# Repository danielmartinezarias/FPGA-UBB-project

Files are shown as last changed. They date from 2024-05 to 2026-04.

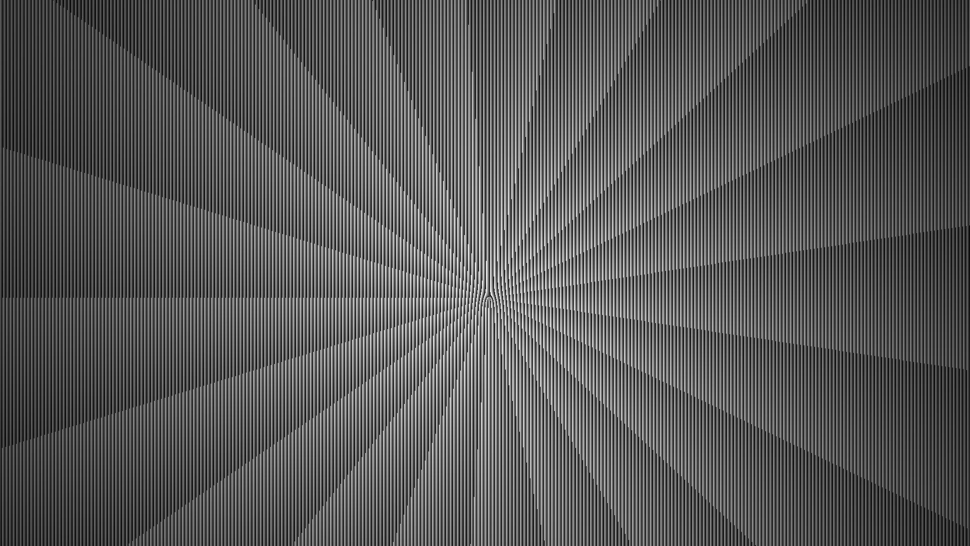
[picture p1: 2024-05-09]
Figuras_Hologramas_OAM/LG_3.jpeg

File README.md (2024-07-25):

# FPGA UBB Quantum Optics Lab
FPGA project for the control system of the OAM experiment. FPGA stores a set of images in a DDR memory, displays such images via HDMI port, prepares a train of short pulses to drive an EOM Intensity modulator, and aquires counts from 2 detectors. This project is meant to work along a GUI written in C#.

1. **electronics** contains the source files for the FMC PCB and the LM7171 AMP PCB. These includes manufacturing files, schematics and PCB outlines
2. **caja** contains a blender file with the mechanical drawings of the plastic box for the project
3. **Figuras_Hologramas_OAM** contains a set of holograms to display, and some images with numbers for calibration
4. **FPGA-Vivado-Project** contains the main Vivado project in `Genesys2_VideoDemoR1` and its sources in `srcs`. You can use the project as it is ot build the project by your own running the *srcs/Genesys2_VideoDemoR1.tcl* file with their respective dependencies and then build your own project. Synthesis, implementation and bitstream generation
5. **GUI** includes the main Graphical User Interface (GUI) to run the program along with the FPGA project. C# project in `SOFTWARE BASE-UART` and final GUI in `FINAL`. Notice that a USB UART connection is required to transmit information from the FPGA to PC 115200 buad rate.

## GUI
C# project in `GUI\SOFTWARE BASE-UART\` and FINAL Graphical User  Interface (GUI), located in `GUI\SOFTWARE BASE-UART\driver_PM_software\bin\Debug\driver_PM_software.exe`
**GUI controls**
- SOON TO BE UPDATED

## FPGA
- Main Vivado project in `FPGA-Vivado-Project\Genesys2_VideoDemoR1`, 
    - Final bitstream is located in `FPGA-Vivado-Project\Genesys2_VideoDemoR1\Genesys2_VideoDemoR1.runs\impl_1\*.bit`. 
    - You can upload this file into the FPGA using Vivado. Left bottom menu, PROGRAM AND DEBUG, Open Hardware, Auto connect, Program FPGA (with the .bit file)
- `srcs` contains all verilog files, please keep this updated

### How to use this repo?
- Create a GitHub account
- Download Github desktop
- CLONE the repository (ask me for access since it is a private repo)
    - If you want to use this files and not modify them CLONE this repository in the MAIN branch. 
    - If you want to modify it create a new branch and have fun
- Now all the files are in the folder where you cloned the repo.
- If you want to make permanet changes to the MAIN branch, make a commit, but ask me first
- GitHub is not meant to store experiment data, but code, keep this repo as clean as possible.

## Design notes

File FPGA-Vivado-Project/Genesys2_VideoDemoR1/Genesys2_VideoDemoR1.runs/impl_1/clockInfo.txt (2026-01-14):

-------------------------------------
| Tool Version : Vivado v.2023.2
| Date         : Wed Jan 14 18:05:04 2026
| Host         : LAPTOP-RR96MLV1
| Design       : design_1
| Device       : xc7k325t-ffg900-2--
-------------------------------------

For more information on clockInfo.txt clock routing debug file see https://support.xilinx.com/s/article/000035660?language=en_US

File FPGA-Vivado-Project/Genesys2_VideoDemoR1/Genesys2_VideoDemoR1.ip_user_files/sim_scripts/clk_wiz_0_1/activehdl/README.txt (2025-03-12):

################################################################################
# Vivado (TM) v2023.2 (64-bit)
#
# README.txt: Please read the sections below to understand the steps required to
#             run the exported script and how to fetch design source file details
#             from the file_info.txt file.
#
# Generated by export_simulation on Wed Mar 12 15:34:58 +0100 2025
#
################################################################################

1. Steps to run the generated simulation script

From the shell prompt in the current directory, issue the following command:-

./clk_wiz_0.sh

This command will launch the 'compile', 'elaborate' and 'simulate' functions
implemented in the script file for the 3-step flow. These functions are called
from the main 'run' function in the script file.

The 'run' function first calls the 'check_args' function, the purpose of which
is to verify the generated script arguments and print error if incorrect switch
is specified. The 'run' function then calls the 'setup' function, the purpose of
which is to specify custom or initialization commands. The function also executes
following sub-functions:-
'reset_run' if -reset_run switch is specified.
'reset_log' if -reset_log switch is specified.

The purpose of 'reset_run' function' is to delete the simulator generated design
data from the previous run and the purpose of 'reset_log' function' is to delete
the simulator generated log files.

The 'run' function then calls the 'init_lib' function, the purpose of which is to
create design library mappings and directories. This function is called before the
'compile' step. By default, if '-step' switch is specified with the script then the
script will execute that specfic step, else it will execute all steps applicable
for the target simulator.

For more information on the script, please type './clk_wiz_0.sh -help'

2. Design source file information

export_simulation generates a 'file_info.txt' file that contains design file information
based on the compile order when export_simulation was executed from Vivado. The file
contains information about the file name, type, library it is compiled into, whether
it is part of the IP, associated library, file path information in a comma separated
format. This file can be parsed to extract the required information for generating a
custom script or can be read from verification test infra.

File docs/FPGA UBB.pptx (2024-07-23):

## FPGA UBB

11-03-2024

## Genesys2_VideoDemoR1

- Display_clocks
  - Senales de reloj para video
- Dpti_ctrl
  - Interfaz entre USB-JTAG y memoria DDR para imagenes
- DDR
  - Memoria para guardar 112 imagenes 1920x1080p
- DVID
  - Video interface (HDMI)
- VideoLineBuffer
  - Video buffer
- Video_sync_gen
  - Video signals

## Genesys2_VideoDemoR1

- Sync_pulse_det
  - Genera el sync general, el pulso para el intensity mod (y el trigger para det pero esta obsoleto)
- PmodDA2
  - Controla el bias para el intensity modulator
- Tick_gen
  - Controla el reloj para la comunicacion serial
- UART_RX
  - Recibe parametros del computador via el USB-UART
- UART_Tx
  - Envia datos desde la FPGA hasta el PC
- Control_Parametros
  - Actualiza los parametros dentro de la FPGA
- AccCuentas
  - Adquiere la data de los detectors y suma un cierto numero de eventos en un registro
- Control_DM
  - Controla la secuencia del experimento

## Control_DM

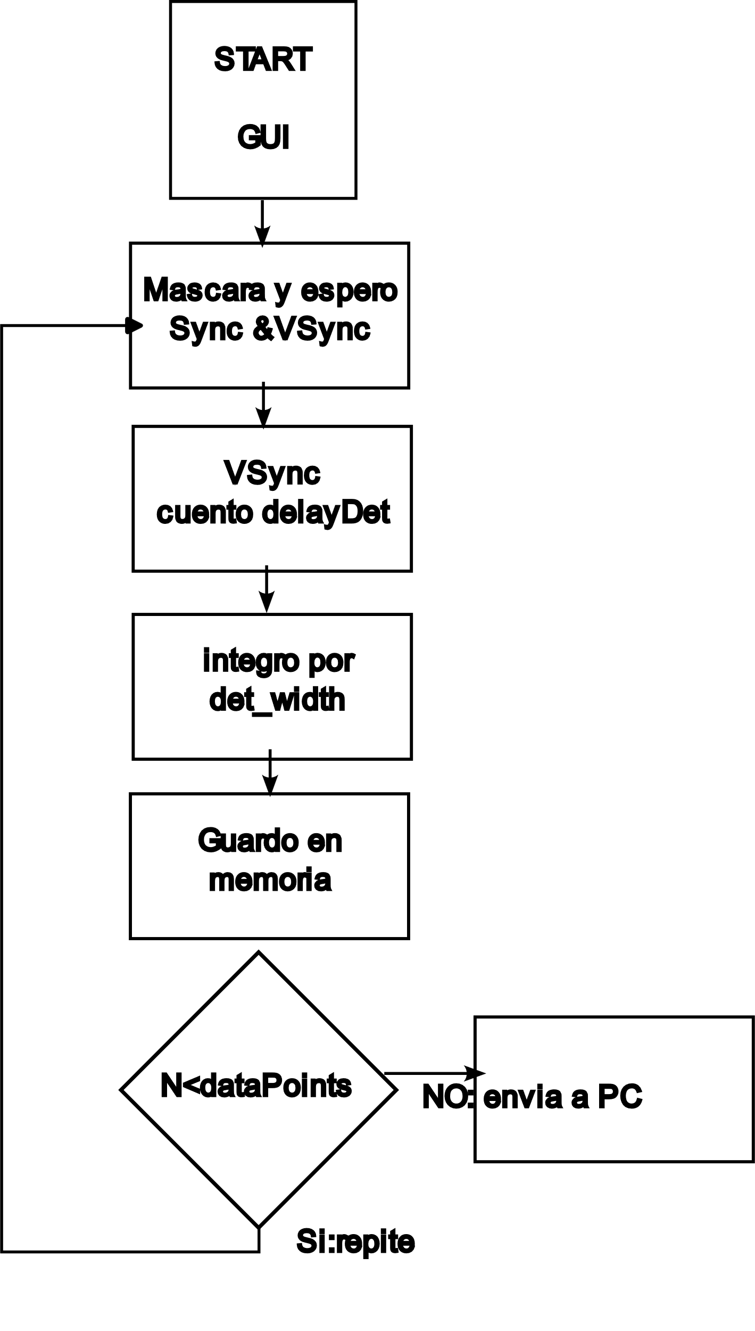
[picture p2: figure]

Falta la generacion del pulso …

## TO DO

- Definir cuantos pulsos por frame/ 1 pulso por frame pero dejar listo para hacer N pulsos por frame
- Necesitamos info pulso a pulso? Si
- Como muestro la data en programa? Se queda en standby
- Pendiente Cargar secuencia aleatoria de sequre

## Daniel

- PCB FMC mezzanine para mejorar data
- Hacer en eurocircuits y comparer project con Gustavo
- Sincronizar las FPGA
- Crear Proyecto en github

## Cristobal

- Cargar el bitstream FPGA_UBB\Final_FPGA_UBB\Genesys2_VideoDemoR1\Genesys2_VideoDemoR1.runs\impl_1\Genesys2_VideoDemoR1.bit en la FPGA
- Correr el GUI que esta en \FPGA_UBB\Final_FPGA_UBB\SOFTWARE BASE-UART\driver_PM_software\bin\Debug\ driver_PM_software.exe

## Cristobal (Para pulso optico)

- Colocar SW(0) = 1
- En GUI Start, luego Monitorear el Puerto LA18_P_CC en osciloscopio. Debe ser pulso cuadrado aprox 1.8V, frecuencia dada por el parametro en GUI. Luego pasar el pulso por el AMP y ajustar para IM.
- Pulsar el IM, evaluar la maxima velocidad, detectando con un fotodiodo y visualizando con osciloscopio

## Cristobal (detector)

- Usar un generador de funciones, preparar un pulso 0-1.8V corto, parecido al pulso que genera el IDQCube, f = 1MHz, output pulse width = 10 ns. Conectar a LA01_PCC (det0) y en el GUI click en START. Width_det = 10000 (10us). Deberias ver 10 cuentas en el GUI
- Repetir conectando en el siguiente Puerto de entrada LA01_P_CC (en realidad es LA17)(det1)

## 27.06.23

- Cristobal probo y valido las detecciones.
- Habia un bug relacionado al reloj pero ya se arreglo

## 28.06.24

- Alice con SW0 = 1, BOB SW0 = 0
- Conectar sync(fmc_la_p_00) de ALICE a sync_ext(fmc_la_p_32) de BOB para que la senal sync de Alice vaya a Bob
- En Alice monitorear el sync(fmc_la_p_04) y MZI(fmc_la_p_18) en osciloscopio. Usar sync como trigger
- En Bob monitorear el det (fmc_la_p_24) que corresponde al tiempo de medicion.
- Ajustar el delay_pulse hasta que alcance a det

## 28.06.24

- Conectar el laser, modulador de intensidad, senal MZI y BIAS
- Conectar detector, y usar en modo trigger
- Mover el delay_det hasta que se maximizen las cuentas

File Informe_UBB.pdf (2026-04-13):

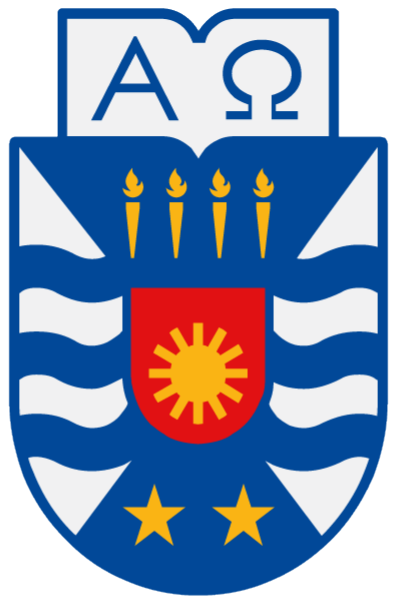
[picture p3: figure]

# Uso del Software de Control

Cristóbal Melo Dospital y Daniel Martinez

1 de abril de 2025

Universidad del Bío-Bío

### Índice

1. Introducción | 2
2. Uso de GitHub Desktop para clonar y mantener actualizado el proyecto | 2
2.1. Clonar el repositorio | | 2
2.2. Sincronizar el repositorio | | 3
2.3. Subir cambios al repositorio | | 4
3. Funcionamiento del Programa | 4
4. Carga del Bitstream a la FPGA | 5
5. Pinout de la Tarjeta FMC | 7
5.1. Salidas desde Alice | | 7
5.2. Entradas hacia Bob | | 7
6. Uso del Software de Control | 8
6.1. Conexión al puerto COM | | 8

### 1. Introducción

Este informe tiene como objetivo documentar el funcionamiento general del programa desarrollado para el control de señales en una FPGA, incluyendo el proceso de carga del bitstream y el uso de la interfaz de software.

### 2. Uso de GitHub Desktop para clonar y mantener actualizado el proyecto

A continuación se detallan los pasos para clonar un repositorio, sincronizar cambios y mantener actualizado el proyecto:

### 2.1. Clonar el repositorio

Opción A: Clonar usando GitHub Desktop vía URL

1. Abre GitHub Desktop.
2. En la barra superior, haz clic en File >Clone repository.

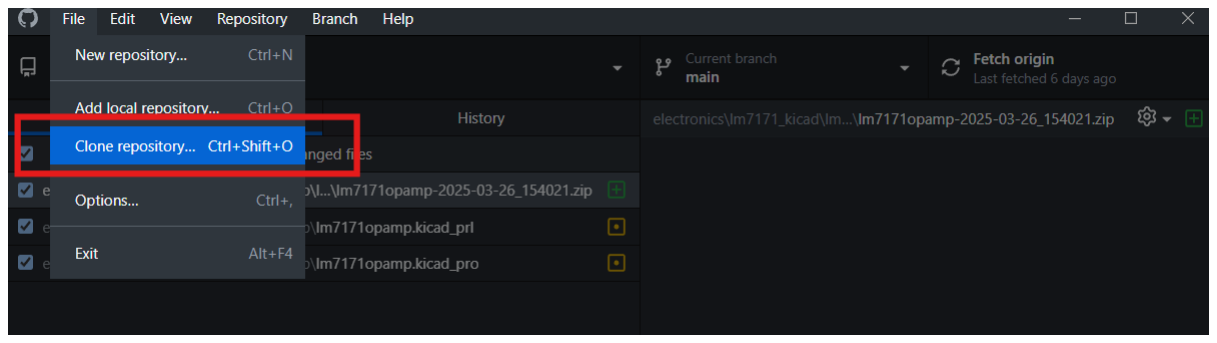
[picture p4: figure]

Figura 1: Clone repository usando Github Desktop

3. En la pestaña URL, pega la dirección del repositorio que deseas clonar (por ejemplo:

https://github.com/usuario/proyecto.git

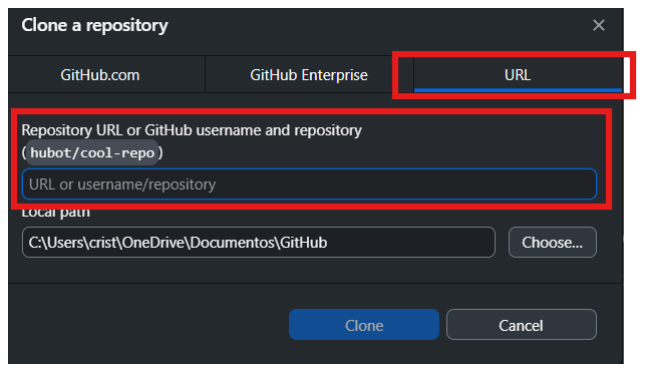
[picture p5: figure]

Figura 2: Ejemplo de clonar repositorio utilizando URL

4. Selecciona la ubicación en tu computador donde se guardará el repositorio localmente.
5. Haz clic en Clone.

Opción B: Clonar directamente desde GitHub.com (usando cuenta vinculada)

1. Abre GitHub Desktop e inicia sesión con tu cuenta de GitHub.
2. Haz clic en File >Clone repository.
3. En la pestaña GitHub.com, aparecerá automáticamente la lista de proyectos disponibles para clonar desde tu cuenta.

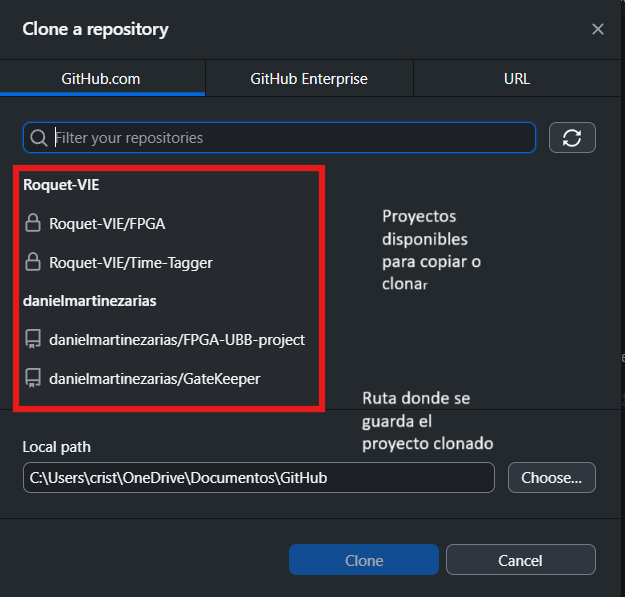
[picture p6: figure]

Figura 3: Ejemplo de clonar repositorio utilizando proyectos de Github.com

4. Selecciona el repositorio que desees clonar de la lista.
5. Elige la carpeta local donde se almacenará el proyecto.
6. Haz clic en Clone.

### 2.2. Sincronizar el repositorio

Una vez clonado, puedes sincronizar tu repositorio local con la versión para ver si hay cambios nuevos (pull) o si puedes subir tus cambios (push).

Presiona el botón Fetch origin en la parte superior. Esto verifica si hay cambios en el repositorio remoto.

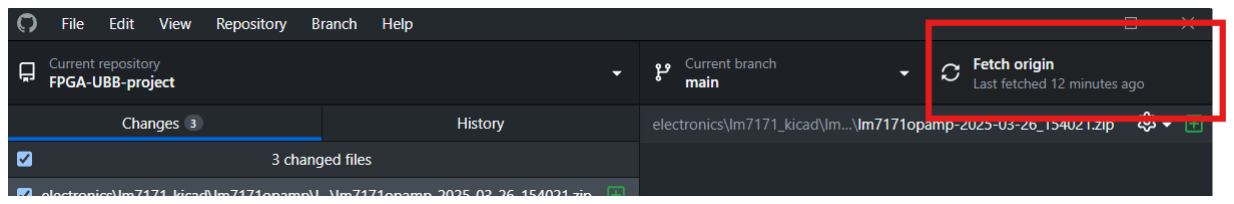
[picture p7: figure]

Figura 4: Sincronizar el repositorio.

Si existen nuevos archivos o modificaciones, el botón cambiará a Pull origin. Haz clic en él para traer los cambios a tu computador.

Si se realizo cambios en tu computador (por ejemplo, editaste archivos del proyecto de Vivado), verás la opción de Commit to main y luego Push origin para subirlos a GitHub (ver Fig. 5).

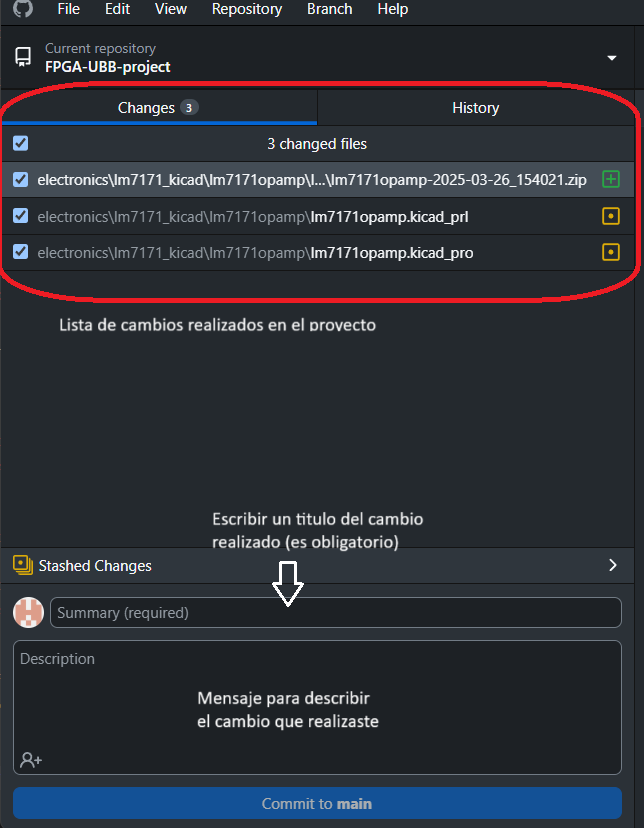
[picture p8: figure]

Figura 5: Ejemplo de cambios realizados al proyecto.

### 2.3. Subir cambios al repositorio

Cuando hayas editado archivos localmente:

1. GitHub Desktop mostrará una lista de archivos modificados.
2. Puedes escribir un mensaje en el cuadro de texto inferior para describir el cambio (por ejemplo: Actualización del archivo .xdc para pines de salida).
3. Luego haz clic en Commit to main.
4. Finalmente, presiona Push origin para subir esos cambios al repositorio remoto en GitHub.

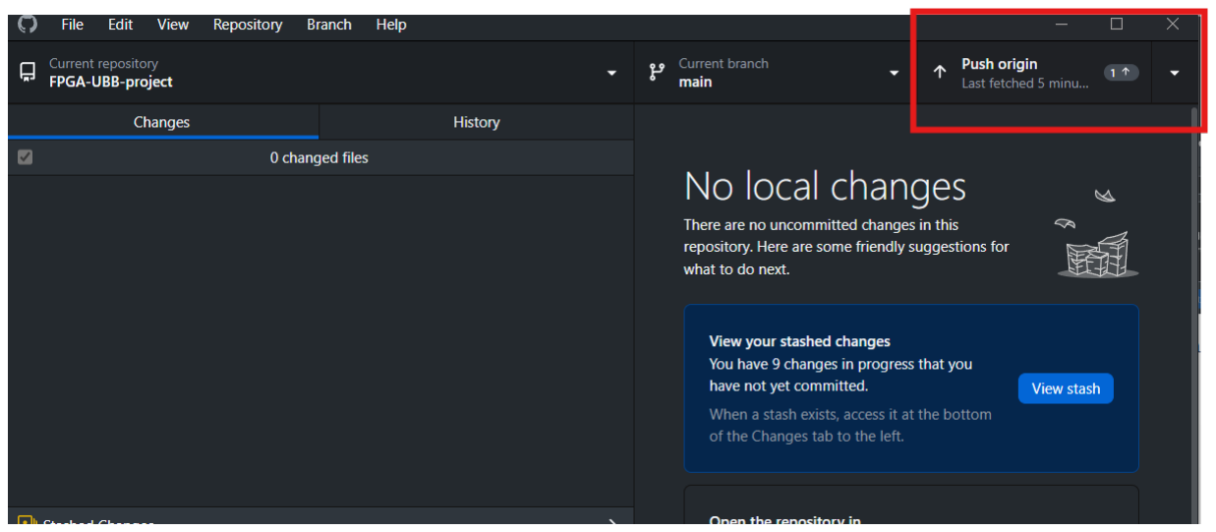
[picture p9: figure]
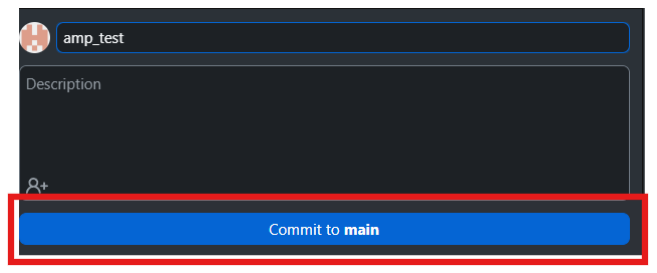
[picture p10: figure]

(a) Boton para hacer Commit. | (b) Botón para hacer push al repositorio remoto.

Figura 6: Interfaz de GitHub Desktop mostrando cómo registrar un cambio y subirlo al repositorio.

### 3. Funcionamiento del Programa

El programa desarrollado permite controlar la generación de señales cuadradas desde una FPGA mediante una interfaz gráfica. Cada señal tiene parámetros configurables como frecuencia, retardo y ancho de pulso. Estos valores se pueden modificar desde el software mediante botones y cuadros numéricos.

El software está desarrollado en C# utilizando Visual Studio 2019.

La comunicación con la FPGA se realiza vía puerto serial.

Cada parámetro se envía codificado usando comandos con identificadores ID específicos.

### 4. Carga del Bitstream a la FPGA

Para programar la FPGA Genesys 2, es fundamental contar con el software Vivado 2023.2 pre-viamente instalado en el equipo.
Una vez abierto Vivado, sigue estos pasos para cargar el archivo .bit:
1. En la pantalla de inicio de Vivado, haz clic en la opción Open Hardware Manager.

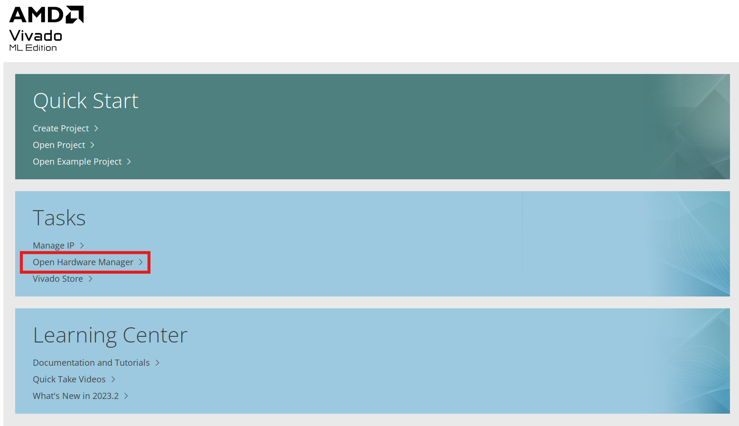
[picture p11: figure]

Figura 7: Acceso a Open Hardware Manager en Vivado.

2. Luego, dirigirse a la parte superior izquierda y haz clic en Open Target. Se desplegará un menú donde debes seleccionar Auto Connect. Esto permite que Vivado detecte automáticamente la tarjeta conectada por USB.

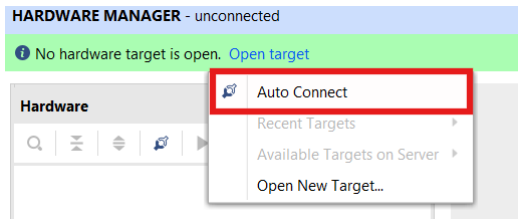
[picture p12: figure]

Figura 8: Conexión automática a la FPGA mediante Auto Connect.

3. Una vez establecida la conexión, selecciona la opción Program Device.

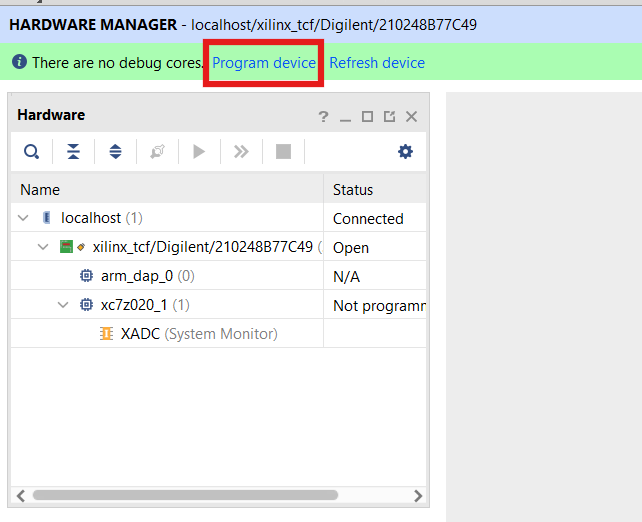
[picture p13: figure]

Figura 9: Selección de la opción Program Device.

4. En la ventana emergente, haz clic en el botón de los tres puntos para explorar tu sistema de archivos y localizar el bitstream.

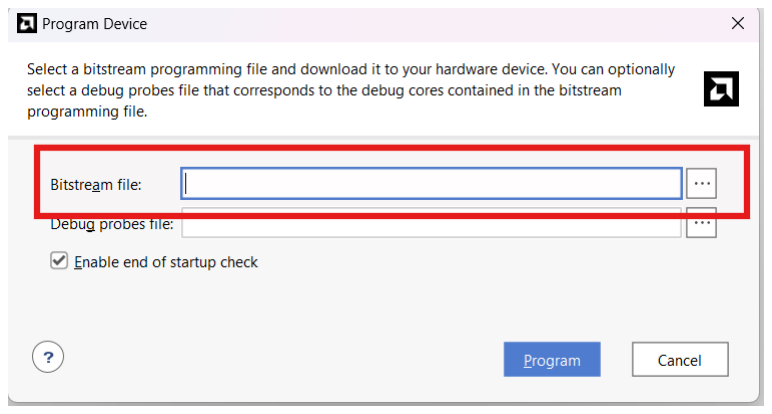
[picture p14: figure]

Figura 10: Navegar para seleccionar manualmente el archivo .bit.

5. Navega hasta la siguiente ruta:

C:\Users\Documentos\GitHub\FPGA-UBB-project\FPGA-Vivado-Project\ Genesys2_VideoDemoR1\Genesys2_VideoDemoR1.runs\impl_1

Selecciona el archivo con extensión .bit correspondiente a tu diseño.

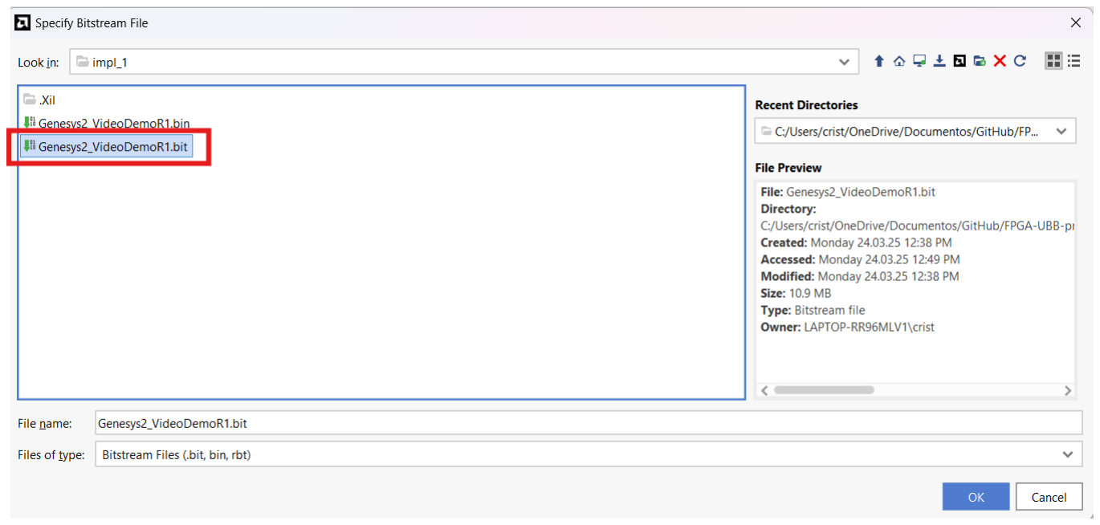
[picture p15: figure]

Figura 11: Ubicación del archivo .bit en el sistema de archivos.

6. Finalmente, haz clic en el botón OK y espera a que Vivado confirme que la carga ha sido exitosa.

### 5. Pinout de la Tarjeta FMC

En la Fig. 12 se muestra la tarjeta utilizada para la conexión entre la FPGA y el Setup a través del conector FMC. Esta tarjeta verde permite la entrada y salida de señales digitales para sincronización, control de moduladores, y adquisición de datos de detección.

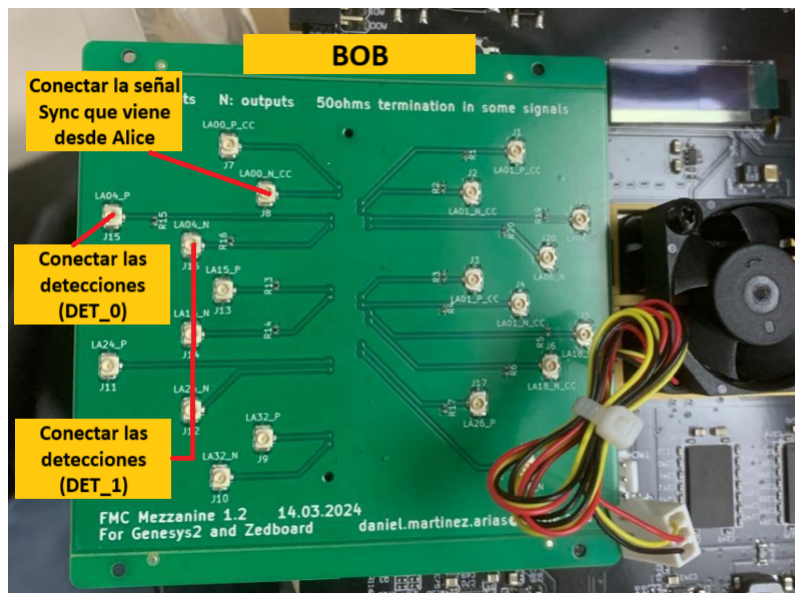
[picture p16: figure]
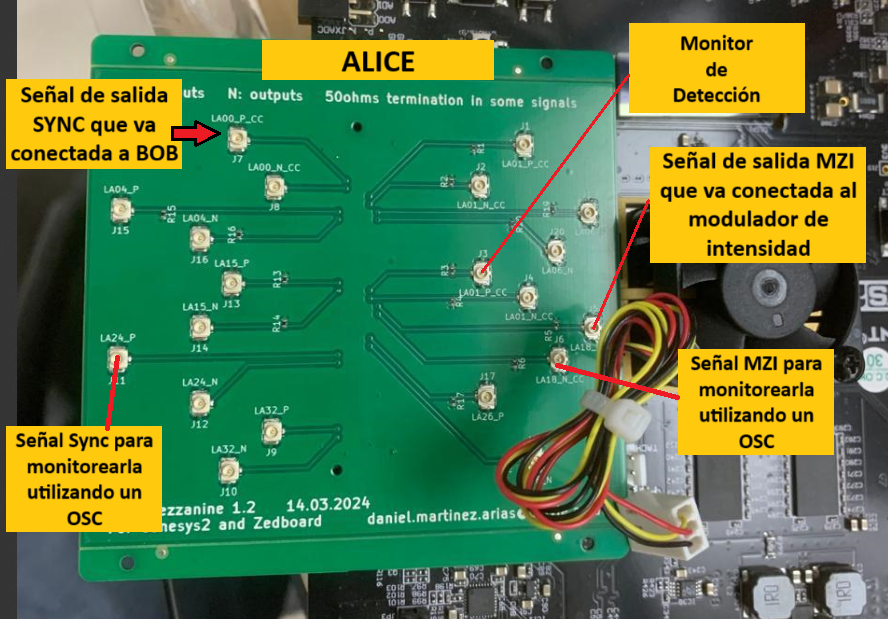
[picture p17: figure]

(a) Pinout correspondiente a la FPGA de Alice. | (b) Pinout correspondiente a la FPGA de Bob.

Figura 12: Distribución de pines de entrada y salida para las tarjetas FMC conectadas a las FPGAs de Alice y Bob.

### 5.1. Salidas desde Alice

La FPGA que representa a Alice genera las siguientes señales de salida desde su FMC:

SYNC: Pulso digital de sincronización enviado hacia Bob. Este pulso permite al sistema de Bob estar alineado temporalmente con Alice.

MZI (o Tren de pulsos para el MZI): Señal periódica destinada a activar el modulador de fase (Mach-Zehnder Interferometer).

Máscara: Señal de referencia que indica qué máscara está activa.

### 5.2. Entradas hacia Bob

La FPGA correspondiente a Bob recibe las siguientes señales mediante su FMC:

SYNC (desde Alice): Señal de entrada recibida desde Alice. Permite sincronizar internamente los sistemas de adquisición y generación de señales en Bob respecto a Alice.

Detección 1 (Det0): Señal digital que representa los pulsos de detección del primer canal.

Detección 2 (Det1): Señal digital correspondiente al segundo canal.

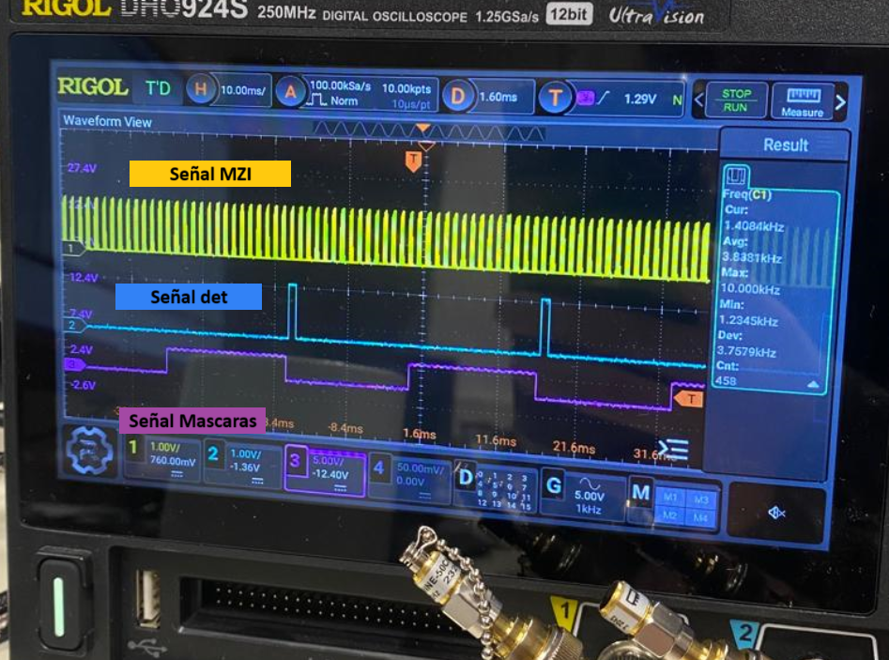
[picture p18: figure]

Figura 13: Señales generadas por la FPGA.

### 6. Uso del Software de Control

Una vez cargado el bitstream en la FPGA, el primer paso es establecer la conexión con el software de control.
El ejecutable se encuentra en la siguiente dirección:

C:\Users\Documentos\GitHub\FPGA-UBB-project\GUI\SOFTWARE BASE-UART\ driver_PM_software\bin\Debug

Dentro de esta carpeta, debes abrir el archivo driver_PM_software.exe para lanzar la interfaz gráfica del programa (ver Fig. 14).

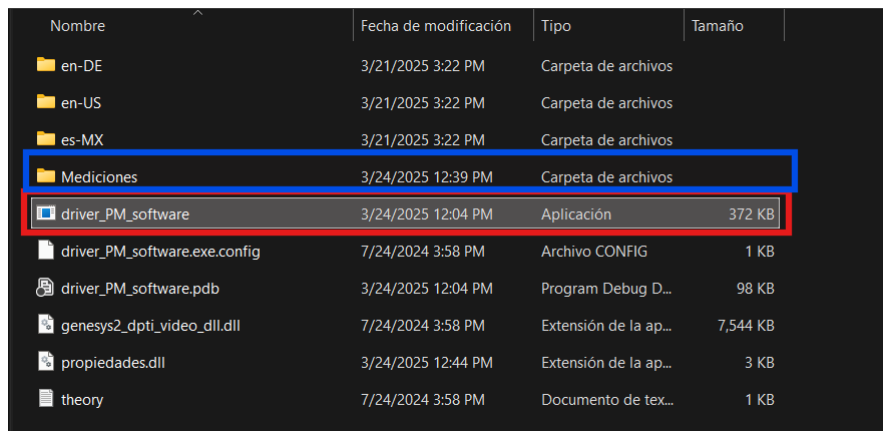
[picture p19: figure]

Figura 14: Ventana principal del software driver_PM_software.exe.

### 6.1. Conexión al puerto COM

Haz clic en la pestaña “COM” (ver Fig.15) del menú superior.

Selecciona el puerto COM correspondiente a tu FPGA.

La conexión debe realizarse a 115200 baudios.

Si no aparece correctamente configurado:

- Abre el Administrador de dispositivos en Windows.
- Ve a “Puertos (COM y LPT)” , haz clic derecho en el puerto correspondiente.
- Selecciona “Propiedades >Configuración del puerto >Velocidad en baudios” y cámbialo a 115200.
- Presiona Aplicar y reinicia el software si es necesario.

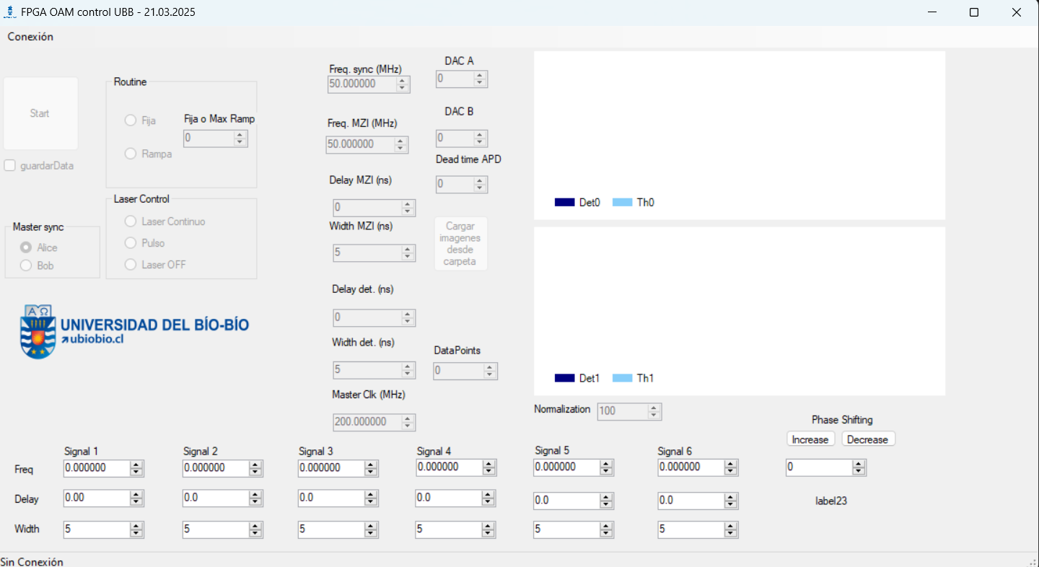
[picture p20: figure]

Figura 15: Interfaz del software de control

Elementos principales

Start: Inicia la generación de señales.

guardarData: Marca para poder almacenar datos durante la ejecución.

Routine: Permite seleccionar entre modo fijo o rampa.

- Fija o Max Ramp: Usa el numericUpDown para elegir la imagen a mostrar de forma fija.
- Rampa: Cambia automáticamente las imágenes a 60 Hz.

Laser Control: Controla el estado del láser (continuo, pulso o apagado).

Master sync: Selección del canal de sincronización maestro (Alice o Bob).

Freq. sync / Freq. MZI: Configura la frecuencia de sincronización o del MZI.

Delay / Width MZI y Det: Configura retardo y ancho del pulso en el MZI y el detector.

DataPoints: Cantidad de muestras a capturar por adquisición.

Signal 1–6: Configura las seis señales independientes:

- Frecuencia
- Retardo (delay)
- Ancho del pulso (width)

Phase Shifting: Controla el desplazamiento de fase. Puede incrementar o disminuir mediante los botones Increase y Decrease. El valor numérico representa el número de pasos.

Master Clk: Indica la frecuencia del reloj maestro (fijo en 200 MHz).

Cargar imágenes desde carpeta: Importa datos desde una carpeta para visualización o pro-cesamiento.

DAC A: Controla la tensión de bias de los moduladores MZI (para frecuencias bajas, dejarlo en 642).

Los gráficos a la derecha muestran los conteos en los detectores:

Det0 / Det1: Detecciones activas.

En la Figura 14, el recuadro azul que aparece en la parte derecha de la interfaz corresponde a la zona donde se visualizan y almacenan las mediciones realizadas por la FPGA. Al presionar el botón “guardarData” , el sistema guarda automáticamente un archivo con nombre del tipo:

FPGA_stored_data_2025-03-24_11_32_33

Este nombre indica que la medición fue realizada el 24 de marzo de 2025 a las 11:32:33 horas.

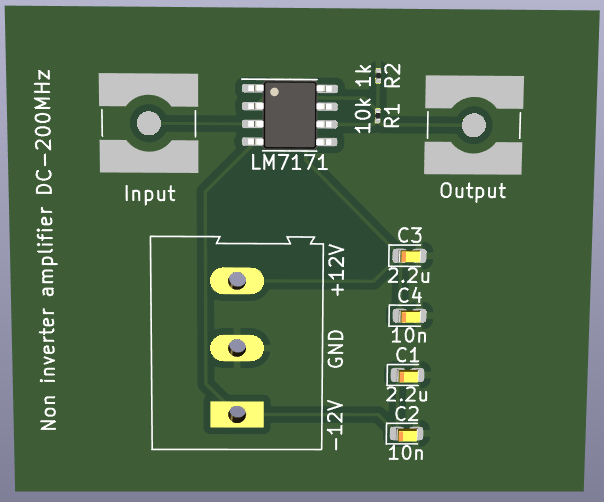
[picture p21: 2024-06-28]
electronics/lm7171_kicad/lm7171opamp/Screenshot 2024-06-12 115450.png

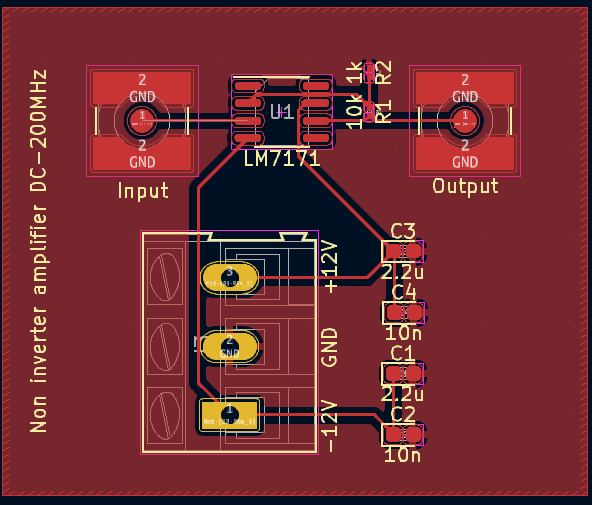
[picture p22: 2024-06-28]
electronics/lm7171_kicad/lm7171opamp/Screenshot 2024-06-12 115400.png

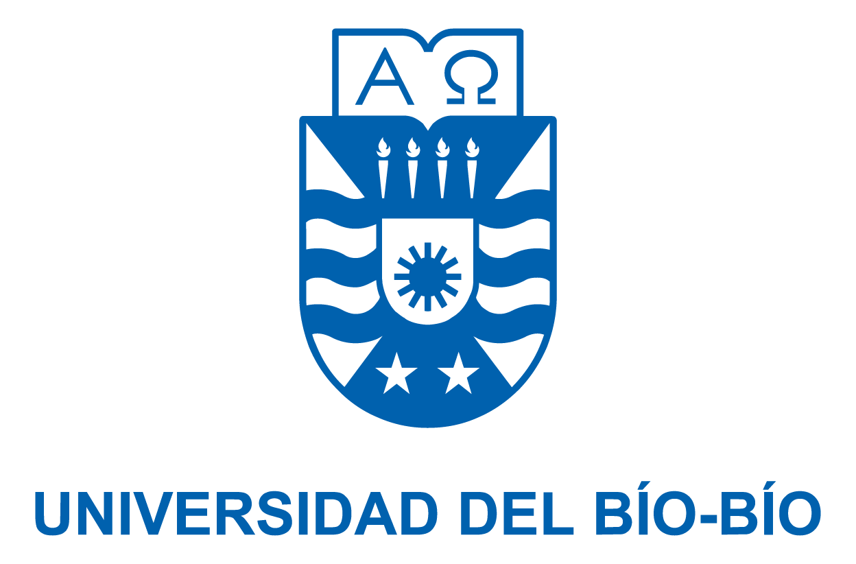
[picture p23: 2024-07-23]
GUI/SOFTWARE BASE-UART/driver_PM_software/escudo-monocromatico.png

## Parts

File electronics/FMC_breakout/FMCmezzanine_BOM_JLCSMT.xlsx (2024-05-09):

Comment | Designator | Footprint | JLCPCB Part #（optional）
50ohm | R1,R2,R3,R4,R5,R6,R13,R14,R15,R16,R17,R18,R19,R20 | R_0402_1005Metric | C853312
 | J1,J2,J3,J4,J5,J6,J7,J8,J9,J10,J11,J12,J13,J14,J15,J16,J17,J18,J19,J20 | Connector_Coaxial:U.FL_Hirose_U.FL-R-SMT-1_Vertical | C434812
Samtec_ASP-134602-01 | J0 | Connector_Samtec:Samtec_FMC_ASP-134602-01_10x40_P1.27mm_Vertical | C2875619

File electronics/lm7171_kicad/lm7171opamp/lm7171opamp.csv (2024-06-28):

Id | Designator | Footprint | Quantity | Designation | Supplier and ref
1 | R1 | R_0201_0603Metric | 1 | 10k
2 | C2,C4 | CP_EIA-1608-08_AVX-J | 2 | 10n
3 | U1 | SOIC-8_3.9x4.9mm_P1.27mm | 1 | LM7171
4 | C3,C1 | CP_EIA-1608-08_AVX-J | 2 | 2.2u
5 | J3 | TerminalBlock_Altech_AK300-3_P5.00mm | 1 | -12V GND +12V
6 | J1 | SMA_Amphenol_132134-10_Vertical | 1 | Input
7 | R2 | R_0201_0603Metric | 1 | 1k
8 | J2 | SMA_Amphenol_132134-10_Vertical | 1 | Output

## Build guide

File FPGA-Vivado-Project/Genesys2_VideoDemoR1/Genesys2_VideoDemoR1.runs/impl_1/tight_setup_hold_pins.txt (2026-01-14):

+====================+====================+===============================================================================================================================================================================================================================================+
| Launch Setup Clock | Launch Hold Clock  | Pin                                                                                                                                                                                                                                           |
+====================+====================+===============================================================================================================================================================================================================================================+
| clk_out4_clk_wiz_0 | clk_out4_clk_wiz_0 | ureg_1_reg[19]/D                                                                                                                                                                                                                              |
| clk_out4_clk_wiz_0 | clk_out4_clk_wiz_0 | ureg_1_reg[0]/D                                                                                                                                                                                                                               |
| clk_out4_clk_wiz_0 | clk_out4_clk_wiz_0 | ureg_1_reg[12]/D                                                                                                                                                                                                                              |
| clk_out4_clk_wiz_0 | clk_out4_clk_wiz_0 | ureg_1_reg[22]/D                                                                                                                                                                                                                              |
| clk_out4_clk_wiz_0 | clk_out4_clk_wiz_0 | ureg_1_reg[14]/D                                                                                                                                                                                                                              |
| clk_out4_clk_wiz_0 | clk_out4_clk_wiz_0 | ureg_1_reg[0]/CE                                                                                                                                                                                                                              |
| clk_out4_clk_wiz_0 | clk_out4_clk_wiz_0 | ureg_1_reg[20]/CE                                                                                                                                                                                                                             |
| clk_out4_clk_wiz_0 | clk_out4_clk_wiz_0 | ureg_1_reg[19]/CE                                                                                                                                                                                                                             |
| clk_out4_clk_wiz_0 | clk_out4_clk_wiz_0 | ureg_1_reg[25]/CE                                                                                                                                                                                                                             |
| clk_out4_clk_wiz_0 | clk_out4_clk_wiz_0 | ureg_1_reg[24]/CE                                                                                                                                                                                                                             |
| clk_out4_clk_wiz_0 | clk_out4_clk_wiz_0 | ureg_1_reg[23]/CE                                                                                                                                                                                                                             |
| clk_out4_clk_wiz_0 | clk_out4_clk_wiz_0 | ureg_1_reg[22]/CE                                                                                                                                                                                                                             |
| clk_out4_clk_wiz_0 | clk_out4_clk_wiz_0 | ureg_1_reg[12]/CE                                                                                                                                                                                                                             |
| clk_out4_clk_wiz_0 | clk_out4_clk_wiz_0 | ureg_1_reg[28]/CE                                                                                                                                                                                                                             |
| clk_out4_clk_wiz_0 | clk_out4_clk_wiz_0 | ureg_1_reg[27]/CE                                                                                                                                                                                                                             |
| clk_out4_clk_wiz_0 | clk_out4_clk_wiz_0 | ureg_1_reg[21]/CE                                                                                                                                                                                                                             |
| clk_out4_clk_wiz_0 | clk_out4_clk_wiz_0 | ureg_1_reg[18]/D                                                                                                                                                                                                                              |
| clk_out4_clk_wiz_0 | clk_out4_clk_wiz_0 | ureg_1_reg[28]/D                                                                                                                                                                                                                              |
| clk_out4_clk_wiz_0 | clk_out4_clk_wiz_0 | ureg_1_reg[6]/CE                                                                                                                                                                                                                              |
| clk_out4_clk_wiz_0 | clk_out4_clk_wiz_0 | ureg_1_reg[26]/CE                                                                                                                                                                                                                             |
| clk_out4_clk_wiz_0 | clk_out4_clk_wiz_0 | ureg_1_reg[4]/CE                                                                                                                                                                                                                              |
| clk_out4_clk_wiz_0 | clk_out4_clk_wiz_0 | ureg_1_reg[16]/CE                                                                                                                                                                                                                             |
| clk_out4_clk_wiz_0 | clk_out4_clk_wiz_0 | ureg_1_reg[5]/CE                                                                                                                                                                                                                              |
| clk_out4_clk_wiz_0 | clk_out4_clk_wiz_0 | ureg_1_reg[10]/CE                                                                                                                                                                                                                             |
| clk_out4_clk_wiz_0 | clk_out4_clk_wiz_0 | ureg_1_reg[7]/CE                                                                                                                                                                                                                              |
| clk_out4_clk_wiz_0 | clk_out4_clk_wiz_0 | ureg_1_reg[17]/CE                                                                                                                                                                                                                             |
| clk_out4_clk_wiz_0 | clk_out4_clk_wiz_0 | ureg_1_reg[13]/CE                                                                                                                                                                                                                             |
| clk_out4_clk_wiz_0 | clk_out4_clk_wiz_0 | ureg_1_reg[2]/CE                                                                                                                                                                                                                              |
| clk_out4_clk_wiz_0 | clk_out4_clk_wiz_0 | ureg_1_reg[3]/CE                                                                                                                                                                                                                              |
| clk_out4_clk_wiz_0 | clk_out4_clk_wiz_0 | ureg_1_reg[11]/CE                                                                                                                                                                                                                             |
| clk_out4_clk_wiz_0 | clk_out4_clk_wiz_0 | ureg_1_reg[1]/CE                                                                                                                                                                                                                              |
| clk_out4_clk_wiz_0 | clk_out4_clk_wiz_0 | ureg_1_reg[9]/CE                                                                                                                                                                                                                              |
| clk_out4_clk_wiz_0 | clk_out4_clk_wiz_0 | ureg_1_reg[8]/CE                                                                                                                                                                                                                              |
| clk_out4_clk_wiz_0 | clk_out4_clk_wiz_0 | ureg_1_reg[15]/D                                                                                                                                                                                                                              |
| clk_out4_clk_wiz_0 | clk_out4_clk_wiz_0 | ureg_1_reg[14]/CE                                                                                                                                                                                                                             |
| clk_out4_clk_wiz_0 | clk_out4_clk_wiz_0 | ureg_1_reg[15]/CE                                                                                                                                                                                                                             |
| clk_out4_clk_wiz_0 | clk_out4_clk_wiz_0 | ureg_1_reg[18]/CE                                                                                                                                                                                                                             |
| clk_out4_clk_wiz_0 | clk_out4_clk_wiz_0 | ureg_1_reg[27]/D                                                                                                                                                                                                                              |
| clk_out4_clk_wiz_0 | clk_out4_clk_wiz_0 | ureg_1_reg[5]/D                                                                                                                                                                                                                               |
| clk_out4_clk_wiz_0 | clk_out4_clk_wiz_0 | ureg_1_reg[2]/D                                                                                                                                                                                                                               |
| clk_out4_clk_wiz_0 | clk_out4_clk_wiz_0 | ureg_1_reg[7]/D                                                                                                                                                                                                                               |
| clk_out4_clk_wiz_0 | clk_out4_clk_wiz_0 | ureg_1_reg[9]/D                                                                                                                                                                                                                               |
| clk_out4_clk_wiz_0 | clk_out4_clk_wiz_0 | ureg_1_reg[4]/D                                                                                                                                                                                                                               |
| clk_out4_clk_wiz_0 | clk_out4_clk_wiz_0 | ureg_1_reg[8]/D                                                                                                                                                                                                                               |
| clk_out4_clk_wiz_0 | clk_out4_clk_wiz_0 | ureg_1_reg[21]/D                                                                                                                                                                                                                              |
| clk_out4_clk_wiz_0 | clk_out4_clk_wiz_0 | ureg_1_reg[3]/D                                                                                                                                                                                                                               |
| clk_out4_clk_wiz_0 | clk_out4_clk_wiz_0 | ureg_1_reg[6]/D                                                                                                                                                                                                                               |
| clk_out4_clk_wiz_0 | clk_out4_clk_wiz_0 | ureg_2_reg[7]/D                                                                                                                                                                                                                               |
| clk_out4_clk_wiz_0 | clk_out4_clk_wiz_0 | ureg_1_reg[23]/D                                                                                                                                                                                                                              |
| clk_out4_clk_wiz_0 | clk_out4_clk_wiz_0 | ureg_2_reg[27]/D                                                                                                                                                                                                                              |
| clk_out4_clk_wiz_0 | clk_out4_clk_wiz_0 | ureg_2_reg[6]/D                                                                                                                                                                                                                               |
| clk_out4_clk_wiz_0 | clk_out4_clk_wiz_0 | ureg_2_reg[16]/D                                                                                                                                                                                                                              |
| clk_out4_clk_wiz_0 | clk_out4_clk_wiz_0 | ureg_2_reg[17]/D                                                                                                                                                                                                                              |
| clk_out4_clk_wiz_0 | clk_out4_clk_wiz_0 | ureg_1_reg[20]/D                                                                                                                                                                                                                              |
| clk_out4_clk_wiz_0 | clk_out4_clk_wiz_0 | ureg_2_reg[22]/D                                                                                                                                                                                                                              |
| clk_out4_clk_wiz_0 | clk_out4_clk_wiz_0 | ureg_2_reg[24]/D                                                                                                                                                                                                                              |
| clk_out4_clk_wiz_0 | clk_out4_clk_wiz_0 | ureg_2_reg[9]/D                                                                                                                                                                                                                               |
| clk_out4_clk_wiz_0 | clk_out4_clk_wiz_0 | ureg_1_reg[24]/D                                                                                                                                                                                                                              |
| clk_out4_clk_wiz_0 | clk_out4_clk_wiz_0 | ureg_2_reg[4]/D                                                                                                                                                                                                                               |
| clk_out4_clk_wiz_0 | clk_out4_clk_wiz_0 | ureg_2_reg[28]/D                                                                                                                                                                                                                              |
| clk_out4_clk_wiz_0 | clk_out4_clk_wiz_0 | ureg_2_reg[26]/D                                                                                                                                                                                                                              |
| clk_out4_clk_wiz_0 | clk_out4_clk_wiz_0 | ureg_2_reg[0]/D                                                                                                                                                                                                                               |
| clk_out4_clk_wiz_0 | clk_out4_clk_wiz_0 | ureg_2_reg[12]/D                                                                                                                                                                                                                              |
| clk_out4_clk_wiz_0 | clk_out4_clk_wiz_0 | ureg_2_reg[8]/D                                                                                                                                                                                                                               |
| clk_out4_clk_wiz_0 | clk_out4_clk_wiz_0 | ureg_2_reg[23]/D                                                                                                                                                                                                                              |
| clk_out4_clk_wiz_0 | clk_out4_clk_wiz_0 | ureg_1_reg[1]/D                                                                                                                                                                                                                               |
| clk_out4_clk_wiz_0 | clk_out4_clk_wiz_0 | ureg_2_reg[5]/D                                                                                                                                                                                                                               |
| clk_out4_clk_wiz_0 | clk_out4_clk_wiz_0 | ureg_2_reg[15]/D                                                                                                                                                                                                                              |
| clk_out4_clk_wiz_0 | clk_out4_clk_wiz_0 | ureg_2_reg[25]/D                                                                                                                                                                                                                              |
| clk_out4_clk_wiz_0 | clk_out4_clk_wiz_0 | ureg_2_reg[3]/D                                                                                                                                                                                                                               |
| clk_out4_clk_wiz_0 | clk_out4_clk_wiz_0 | ureg_2_reg[2]/D                                                                                                                                                                                                                               |
| clk_out4_clk_wiz_0 | clk_out4_clk_wiz_0 | ureg_1_reg[26]/D                                                                                                                                                                                                                              |
| clk_out4_clk_wiz_0 | clk_out4_clk_wiz_0 | ureg_2_reg[20]/D                                                                                                                                                                                                                              |
| clk_out4_clk_wiz_0 | clk_out4_clk_wiz_0 | ureg_2_reg[1]/D                                                                                                                                                                                                                               |
| clk_out4_clk_wiz_0 | clk_out4_clk_wiz_0 | ureg_1_reg[11]/D                                                                                                                                                                                                                              |
| clk_out4_clk_wiz_0 | clk_out4_clk_wiz_0 | ureg_1_reg[16]/D                                                                                                                                                                                                                              |
| clk_out4_clk_wiz_0 | clk_out4_clk_wiz_0 | ureg_1_reg[17]/D                                                                                                                                                                                                                              |
| clk_out4_clk_wiz_0 | clk_out4_clk_wiz_0 | ureg_1_reg[25]/D                                                                                                                                                                                                                              |
| clk_out4_clk_wiz_0 | clk_out4_clk_wiz_0 | ureg_2_reg[21]/D                                                                                                                                                                                                                              |
| clk_out4_clk_wiz_0 | clk_out4_clk_wiz_0 | ureg_2_reg[18]/D                                                                                                                                                                                                                              |
| clk_out4_clk_wiz_0 | clk_out4_clk_wiz_0 | ureg_2_reg[14]/D                                                                                                                                                                                                                              |
| clk_out4_clk_wiz_0 | clk_out4_clk_wiz_0 | ureg_2_reg[13]/D                                                                                                                                                                                                                              |
| clk_out4_clk_wiz_0 | clk_out4_clk_wiz_0 | ureg_2_reg[10]/D                                                                                                                                                                                                                              |
| clk_out4_clk_wiz_0 | clk_out4_clk_wiz_0 | ureg_2_reg[19]/D                                                                                                                                                                                                                              |
| clk_out4_clk_wiz_0 | clk_out4_clk_wiz_0 | ureg_2_reg[11]/D                                                                                                                                                                                                                              |
| clk_out4_clk_wiz_0 | clk_out4_clk_wiz_0 | ureg_1_reg[10]/D                                                                                                                                                                                                                              |
| clk_out4_clk_wiz_0 | clk_out4_clk_wiz_0 | ureg_1_reg[13]/D                                                                                                                                                                                                                              |
| clk_5x_pre         | clk_1x_pre         | Inst_dvid/shift_red_reg[5]/D                                                                                                                                                                                                                  |
| clk_5x_pre         | clk_1x_pre         | Inst_dvid/shift_blue_reg[7]/D                                                                                                                                                                                                                 |
| clk_5x_pre         | clk_1x_pre         | Inst_dvid/shift_green_reg[3]/D                                                                                                                                                                                                                |
| clk_5x_pre         | clk_1x_pre         | Inst_dvid/shift_blue_reg[6]/D                                                                                                                                                                                                                 |
| clk_5x_pre         | clk_1x_pre         | Inst_dvid/shift_blue_reg[1]/D                                                                                                                                                                                                                 |
| clk_5x_pre         | clk_1x_pre         | Inst_dvid/shift_red_reg[4]/D                                                                                                                                                                                                                  |
| clk_5x_pre         | clk_1x_pre         | Inst_dvid/shift_red_reg[2]/D                                                                                                                                                                                                                  |
| clk_5x_pre         | clk_1x_pre         | Inst_dvid/shift_green_reg[5]/D                                                                                                                                                                                                                |
| clk_5x_pre         | clk_1x_pre         | Inst_dvid/shift_blue_reg[3]/D                                                                                                                                                                                                                 |
| clk_5x_pre         | clk_1x_pre         | Inst_dvid/shift_blue_reg[0]/D                                                                                                                                                                                                                 |
| clk_5x_pre         | clk_1x_pre         | Inst_dvid/shift_blue_reg[2]/D                                                                                                                                                                                                                 |
| clk_5x_pre         | clk_1x_pre         | Inst_dvid/shift_green_reg[0]/D                                                                                                                                                                                                                |
| clk_5x_pre         | clk_1x_pre         | Inst_dvid/shift_green_reg[4]/D                                                                                                                                                                                                                |
| clk_5x_pre         | clk_1x_pre         | Inst_dvid/shift_red_reg[0]/D                                                                                                                                                                                                                  |
| clk_5x_pre         | clk_1x_pre         | Inst_dvid/shift_red_reg[3]/D                                                                                                                                                                                                                  |
| clk_5x_pre         | clk_1x_pre         | Inst_dvid/shift_blue_reg[5]/D                                                                                                                                                                                                                 |
| clk_5x_pre         | clk_1x_pre         | Inst_dvid/shift_red_reg[7]/D                                                                                                                                                                                                                  |
| clk_5x_pre         | clk_1x_pre         | Inst_dvid/shift_red_reg[6]/D                                                                                                                                                                                                                  |
| clk_5x_pre         | clk_1x_pre         | Inst_dvid/shift_green_reg[1]/D                                                                                                                                                                                                                |
| clk_5x_pre         | clk_1x_pre         | Inst_dvid/shift_green_reg[7]/D                                                                                                                                                                                                                |
| clk_5x_pre         | clk_1x_pre         | Inst_dvid/shift_green_reg[2]/D                                                                                                                                                                                                                |
| clk_5x_pre         | clk_1x_pre         | Inst_dvid/shift_red_reg[1]/D                                                                                                                                                                                                                  |
| clk_5x_pre         | clk_1x_pre         | Inst_dvid/shift_blue_reg[4]/D                                                                                                                                                                                                                 |
| clk_5x_pre         | clk_1x_pre         | Inst_dvid/shift_green_reg[6]/D                                                                                                                                                                                                                |
| clk_1x_pre         | clk_1x_pre         | Inst_dvid/shift_blue_reg[8]/D                                                                                                                                                                                                                 |
| clk_1x_pre         | clk_1x_pre         | Inst_dvid/shift_blue_reg[9]/D                                                                                                                                                                                                                 |
| clk_1x_pre         | clk_1x_pre         | Inst_dvid/shift_green_reg[8]/D                                                                                                                                                                                                                |
| clk_1x_pre         | clk_1x_pre         | Inst_dvid/shift_red_reg[9]/D                                                                                                                                                                                                                  |
| clk_1x_pre         | clk_1x_pre         | Inst_dvid/shift_green_reg[9]/D                                                                                                                                                                                                                |
| clk_1x_pre         | clk_1x_pre         | Inst_dvid/shift_red_reg[8]/D                                                                                                                                                                                                                  |
| oserdes_clk_1      | oserdes_clk_1      | DDR_INF_inst/u_mig_7series_0_mig/u_memc_ui_top_std/mem_intfc0/ddr_phy_top0/u_ddr_mc_phy_wrapper/u_ddr_mc_phy/ddr_phy_4lanes_0.u_ddr_phy_4lanes/ddr_byte_lane_B.ddr_byte_lane_B/ddr_byte_group_io/output_[8].oserdes_dq_.ddr.oserdes_dq_i/RST  |
| oserdes_clk_2      | oserdes_clk_2      | DDR_INF_inst/u_mig_7series_0_mig/u_memc_ui_top_std/mem_intfc0/ddr_phy_top0/u_ddr_mc_phy_wrapper/u_ddr_mc_phy/ddr_phy_4lanes_0.u_ddr_phy_4lanes/ddr_byte_lane_C.ddr_byte_lane_C/ddr_byte_group_io/output_[2].oserdes_dq_.ddr.oserdes_dq_i/RST  |
| oserdes_clk_6      | oserdes_clk_6      | DDR_INF_inst/u_mig_7series_0_mig/u_memc_ui_top_std/mem_intfc0/ddr_phy_top0/u_ddr_mc_phy_wrapper/u_ddr_mc_phy/ddr_phy_4lanes_1.u_ddr_phy_4lanes/ddr_byte_lane_C.ddr_byte_lane_C/ddr_byte_group_io/output_[2].oserdes_dq_.sdr.oserdes_dq_i/RST  |
| oserdes_clk_1      | oserdes_clk_1      | DDR_INF_inst/u_mig_7series_0_mig/u_memc_ui_top_std/mem_intfc0/ddr_phy_top0/u_ddr_mc_phy_wrapper/u_ddr_mc_phy/ddr_phy_4lanes_0.u_ddr_phy_4lanes/ddr_byte_lane_B.ddr_byte_lane_B/ddr_byte_group_io/output_[6].oserdes_dq_.ddr.oserdes_dq_i/RST  |
| oserdes_clk_2      | oserdes_clk_2      | DDR_INF_inst/u_mig_7series_0_mig/u_memc_ui_top_std/mem_intfc0/ddr_phy_top0/u_ddr_mc_phy_wrapper/u_ddr_mc_phy/ddr_phy_4lanes_0.u_ddr_phy_4lanes/ddr_byte_lane_C.ddr_byte_lane_C/ddr_byte_group_io/output_[4].oserdes_dq_.ddr.oserdes_dq_i/RST  |
| oserdes_clk_6      | oserdes_clk_6      | DDR_INF_inst/u_mig_7series_0_mig/u_memc_ui_top_std/mem_intfc0/ddr_phy_top0/u_ddr_mc_phy_wrapper/u_ddr_mc_phy/ddr_phy_4lanes_1.u_ddr_phy_4lanes/ddr_byte_lane_C.ddr_byte_lane_C/ddr_byte_group_io/output_[4].oserdes_dq_.sdr.oserdes_dq_i/RST  |
| oserdes_clk_1      | oserdes_clk_1      | DDR_INF_inst/u_mig_7series_0_mig/u_memc_ui_top_std/mem_intfc0/ddr_phy_top0/u_ddr_mc_phy_wrapper/u_ddr_mc_phy/ddr_phy_4lanes_0.u_ddr_phy_4lanes/ddr_byte_lane_B.ddr_byte_lane_B/ddr_byte_group_io/output_[9].oserdes_dq_.ddr.oserdes_dq_i/RST  |
| oserdes_clk_3      | oserdes_clk_3      | DDR_INF_inst/u_mig_7series_0_mig/u_memc_ui_top_std/mem_intfc0/ddr_phy_top0/u_ddr_mc_phy_wrapper/u_ddr_mc_phy/ddr_phy_4lanes_0.u_ddr_phy_4lanes/ddr_byte_lane_D.ddr_byte_lane_D/ddr_byte_group_io/output_[1].oserdes_dq_.ddr.oserdes_dq_i/RST  |
| oserdes_clk_3      | oserdes_clk_3      | DDR_INF_inst/u_mig_7series_0_mig/u_memc_ui_top_std/mem_intfc0/ddr_phy_top0/u_ddr_mc_phy_wrapper/u_ddr_mc_phy/ddr_phy_4lanes_0.u_ddr_phy_4lanes/ddr_byte_lane_D.ddr_byte_lane_D/ddr_byte_group_io/output_[2].oserdes_dq_.ddr.oserdes_dq_i/RST  |
| oserdes_clk_7      | oserdes_clk_7      | DDR_INF_inst/u_mig_7series_0_mig/u_memc_ui_top_std/mem_intfc0/ddr_phy_top0/u_ddr_mc_phy_wrapper/u_ddr_mc_phy/ddr_phy_4lanes_1.u_ddr_phy_4lanes/ddr_byte_lane_D.ddr_byte_lane_D/ddr_byte_group_io/output_[2].oserdes_dq_.sdr.oserdes_dq_i/RST  |
| oserdes_clk_7      | oserdes_clk_7      | DDR_INF_inst/u_mig_7series_0_mig/u_memc_ui_top_std/mem_intfc0/ddr_phy_top0/u_ddr_mc_phy_wrapper/u_ddr_mc_phy/ddr_phy_4lanes_1.u_ddr_phy_4lanes/ddr_byte_lane_D.ddr_byte_lane_D/ddr_byte_group_io/output_[1].oserdes_dq_.sdr.oserdes_dq_i/RST  |
| oserdes_clk        | oserdes_clk        | DDR_INF_inst/u_mig_7series_0_mig/u_memc_ui_top_std/mem_intfc0/ddr_phy_top0/u_ddr_mc_phy_wrapper/u_ddr_mc_phy/ddr_phy_4lanes_0.u_ddr_phy_4lanes/ddr_byte_lane_A.ddr_byte_lane_A/ddr_byte_group_io/output_[6].oserdes_dq_.ddr.oserdes_dq_i/RST  |
| oserdes_clk_1      | oserdes_clk_1      | DDR_INF_inst/u_mig_7series_0_mig/u_memc_ui_top_std/mem_intfc0/ddr_phy_top0/u_ddr_mc_phy_wrapper/u_ddr_mc_phy/ddr_phy_4lanes_0.u_ddr_phy_4lanes/ddr_byte_lane_B.ddr_byte_lane_B/ddr_byte_group_io/output_[1].oserdes_dq_.ddr.oserdes_dq_i/RST  |
| oserdes_clk_2      | oserdes_clk_2      | DDR_INF_inst/u_mig_7series_0_mig/u_memc_ui_top_std/mem_intfc0/ddr_phy_top0/u_ddr_mc_phy_wrapper/u_ddr_mc_phy/ddr_phy_4lanes_0.u_ddr_phy_4lanes/ddr_byte_lane_C.ddr_byte_lane_C/ddr_byte_group_io/output_[7].oserdes_dq_.ddr.oserdes_dq_i/RST  |
| oserdes_clk_2      | oserdes_clk_2      | DDR_INF_inst/u_mig_7series_0_mig/u_memc_ui_top_std/mem_intfc0/ddr_phy_top0/u_ddr_mc_phy_wrapper/u_ddr_mc_phy/ddr_phy_4lanes_0.u_ddr_phy_4lanes/ddr_byte_lane_C.ddr_byte_lane_C/ddr_byte_group_io/output_[3].oserdes_dq_.ddr.oserdes_dq_i/RST  |
| oserdes_clk_6      | oserdes_clk_6      | DDR_INF_inst/u_mig_7series_0_mig/u_memc_ui_top_std/mem_intfc0/ddr_phy_top0/u_ddr_mc_phy_wrapper/u_ddr_mc_phy/ddr_phy_4lanes_1.u_ddr_phy_4lanes/ddr_byte_lane_C.ddr_byte_lane_C/ddr_byte_group_io/output_[7].oserdes_dq_.sdr.oserdes_dq_i/RST  |
| oserdes_clk_6      | oserdes_clk_6      | DDR_INF_inst/u_mig_7series_0_mig/u_memc_ui_top_std/mem_intfc0/ddr_phy_top0/u_ddr_mc_phy_wrapper/u_ddr_mc_phy/ddr_phy_4lanes_1.u_ddr_phy_4lanes/ddr_byte_lane_C.ddr_byte_lane_C/ddr_byte_group_io/output_[3].oserdes_dq_.sdr.oserdes_dq_i/RST  |
| oserdes_clk_2      | oserdes_clk_2      | DDR_INF_inst/u_mig_7series_0_mig/u_memc_ui_top_std/mem_intfc0/ddr_phy_top0/u_ddr_mc_phy_wrapper/u_ddr_mc_phy/ddr_phy_4lanes_0.u_ddr_phy_4lanes/ddr_byte_lane_C.ddr_byte_lane_C/ddr_byte_group_io/output_[1].oserdes_dq_.ddr.oserdes_dq_i/RST  |
| oserdes_clk_1      | oserdes_clk_1      | DDR_INF_inst/u_mig_7series_0_mig/u_memc_ui_top_std/mem_intfc0/ddr_phy_top0/u_ddr_mc_phy_wrapper/u_ddr_mc_phy/ddr_phy_4lanes_0.u_ddr_phy_4lanes/ddr_byte_lane_B.ddr_byte_lane_B/ddr_byte_group_io/output_[7].oserdes_dq_.ddr.oserdes_dq_i/RST  |
| oserdes_clk_6      | oserdes_clk_6      | DDR_INF_inst/u_mig_7series_0_mig/u_memc_ui_top_std/mem_intfc0/ddr_phy_top0/u_ddr_mc_phy_wrapper/u_ddr_mc_phy/ddr_phy_4lanes_1.u_ddr_phy_4lanes/ddr_byte_lane_C.ddr_byte_lane_C/ddr_byte_group_io/output_[8].oserdes_dq_.sdr.oserdes_dq_i/RST  |
| oserdes_clk_2      | oserdes_clk_2      | DDR_INF_inst/u_mig_7series_0_mig/u_memc_ui_top_std/mem_intfc0/ddr_phy_top0/u_ddr_mc_phy_wrapper/u_ddr_mc_phy/ddr_phy_4lanes_0.u_ddr_phy_4lanes/ddr_byte_lane_C.ddr_byte_lane_C/ddr_byte_group_io/output_[8].oserdes_dq_.ddr.oserdes_dq_i/RST  |
| oserdes_clk_6      | oserdes_clk_6      | DDR_INF_inst/u_mig_7series_0_mig/u_memc_ui_top_std/mem_intfc0/ddr_phy_top0/u_ddr_mc_phy_wrapper/u_ddr_mc_phy/ddr_phy_4lanes_1.u_ddr_phy_4lanes/ddr_byte_lane_C.ddr_byte_lane_C/ddr_byte_group_io/output_[9].oserdes_dq_.sdr.oserdes_dq_i/RST  |
| oserdes_clk_2      | oserdes_clk_2      | DDR_INF_inst/u_mig_7series_0_mig/u_memc_ui_top_std/mem_intfc0/ddr_phy_top0/u_ddr_mc_phy_wrapper/u_ddr_mc_phy/ddr_phy_4lanes_0.u_ddr_phy_4lanes/ddr_byte_lane_C.ddr_byte_lane_C/ddr_byte_group_io/output_[9].oserdes_dq_.ddr.oserdes_dq_i/RST  |
| oserdes_clk_1      | oserdes_clk_1      | DDR_INF_inst/u_mig_7series_0_mig/u_memc_ui_top_std/mem_intfc0/ddr_phy_top0/u_ddr_mc_phy_wrapper/u_ddr_mc_phy/ddr_phy_4lanes_0.u_ddr_phy_4lanes/ddr_byte_lane_B.ddr_byte_lane_B/ddr_byte_group_io/slave_ts.oserdes_slave_ts/RST                |
| oserdes_clk_5      | oserdes_clk_5      | DDR_INF_inst/u_mig_7series_0_mig/u_memc_ui_top_std/mem_intfc0/ddr_phy_top0/u_ddr_mc_phy_wrapper/u_ddr_mc_phy/ddr_phy_4lanes_1.u_ddr_phy_4lanes/ddr_byte_lane_B.ddr_byte_lane_B/ddr_byte_group_io/output_[10].oserdes_dq_.sdr.oserdes_dq_i/RST |
| oserdes_clk_2      | oserdes_clk_2      | DDR_INF_inst/u_mig_7series_0_mig/u_memc_ui_top_std/mem_intfc0/ddr_phy_top0/u_ddr_mc_phy_wrapper/u_ddr_mc_phy/ddr_phy_4lanes_0.u_ddr_phy_4lanes/ddr_byte_lane_C.ddr_byte_lane_C/ddr_byte_group_io/output_[5].oserdes_dq_.ddr.oserdes_dq_i/RST  |
| oserdes_clk_6      | oserdes_clk_6      | DDR_INF_inst/u_mig_7series_0_mig/u_memc_ui_top_std/mem_intfc0/ddr_phy_top0/u_ddr_mc_phy_wrapper/u_ddr_mc_phy/ddr_phy_4lanes_1.u_ddr_phy_4lanes/ddr_byte_lane_C.ddr_byte_lane_C/ddr_byte_group_io/output_[5].oserdes_dq_.sdr.oserdes_dq_i/RST  |
| oserdes_clk_5      | oserdes_clk_5      | DDR_INF_inst/u_mig_7series_0_mig/u_memc_ui_top_std/mem_intfc0/ddr_phy_top0/u_ddr_mc_phy_wrapper/u_ddr_mc_phy/ddr_phy_4lanes_1.u_ddr_phy_4lanes/ddr_byte_lane_B.ddr_byte_lane_B/ddr_byte_group_io/output_[11].oserdes_dq_.sdr.oserdes_dq_i/RST |
| oserdes_clk_2      | oserdes_clk_2      | DDR_INF_inst/u_mig_7series_0_mig/u_memc_ui_top_std/mem_intfc0/ddr_phy_top0/u_ddr_mc_phy_wrapper/u_ddr_mc_phy/ddr_phy_4lanes_0.u_ddr_phy_4lanes/ddr_byte_lane_C.ddr_byte_lane_C/ddr_byte_group_io/slave_ts.oserdes_slave_ts/RST                |
| oserdes_clk_3      | oserdes_clk_3      | DDR_INF_inst/u_mig_7series_0_mig/u_memc_ui_top_std/mem_intfc0/ddr_phy_top0/u_ddr_mc_phy_wrapper/u_ddr_mc_phy/ddr_phy_4lanes_0.u_ddr_phy_4lanes/ddr_byte_lane_D.ddr_byte_lane_D/ddr_byte_group_io/slave_ts.oserdes_slave_ts/RST                |
| oserdes_clk_6      | oserdes_clk_6      | DDR_INF_inst/u_mig_7series_0_mig/u_memc_ui_top_std/mem_intfc0/ddr_phy_top0/u_ddr_mc_phy_wrapper/u_ddr_mc_phy/ddr_phy_4lanes_1.u_ddr_phy_4lanes/ddr_byte_lane_C.ddr_byte_lane_C/ddr_byte_group_io/output_[10].oserdes_dq_.sdr.oserdes_dq_i/RST |
| oserdes_clk_1      | oserdes_clk_1      | DDR_INF_inst/u_mig_7series_0_mig/u_memc_ui_top_std/mem_intfc0/ddr_phy_top0/u_ddr_mc_phy_wrapper/u_ddr_mc_phy/ddr_phy_4lanes_0.u_ddr_phy_4lanes/ddr_byte_lane_B.ddr_byte_lane_B/ddr_byte_group_io/output_[5].oserdes_dq_.ddr.oserdes_dq_i/RST  |
| oserdes_clk_3      | oserdes_clk_3      | DDR_INF_inst/u_mig_7series_0_mig/u_memc_ui_top_std/mem_intfc0/ddr_phy_top0/u_ddr_mc_phy_wrapper/u_ddr_mc_phy/ddr_phy_4lanes_0.u_ddr_phy_4lanes/ddr_byte_lane_D.ddr_byte_lane_D/ddr_byte_group_io/output_[3].oserdes_dq_.ddr.oserdes_dq_i/RST  |
| oserdes_clk_7      | oserdes_clk_7      | DDR_INF_inst/u_mig_7series_0_mig/u_memc_ui_top_std/mem_intfc0/ddr_phy_top0/u_ddr_mc_phy_wrapper/u_ddr_mc_phy/ddr_phy_4lanes_1.u_ddr_phy_4lanes/ddr_byte_lane_D.ddr_byte_lane_D/ddr_byte_group_io/output_[3].oserdes_dq_.sdr.oserdes_dq_i/RST  |
| oserdes_clk        | oserdes_clk        | DDR_INF_inst/u_mig_7series_0_mig/u_memc_ui_top_std/mem_intfc0/ddr_phy_top0/u_ddr_mc_phy_wrapper/u_ddr_mc_phy/ddr_phy_4lanes_0.u_ddr_phy_4lanes/ddr_byte_lane_A.ddr_byte_lane_A/ddr_byte_group_io/slave_ts.oserdes_slave_ts/RST                |
| oserdes_clk        | oserdes_clk        | DDR_INF_inst/u_mig_7series_0_mig/u_memc_ui_top_std/mem_intfc0/ddr_phy_top0/u_ddr_mc_phy_wrapper/u_ddr_mc_phy/ddr_phy_4lanes_0.u_ddr_phy_4lanes/ddr_byte_lane_A.ddr_byte_lane_A/ddr_byte_group_io/output_[2].oserdes_dq_.ddr.oserdes_dq_i/RST  |
| oserdes_clk        | oserdes_clk        | DDR_INF_inst/u_mig_7series_0_mig/u_memc_ui_top_std/mem_intfc0/ddr_phy_top0/u_ddr_mc_phy_wrapper/u_ddr_mc_phy/ddr_phy_4lanes_0.u_ddr_phy_4lanes/ddr_byte_lane_A.ddr_byte_lane_A/ddr_byte_group_io/output_[4].oserdes_dq_.ddr.oserdes_dq_i/RST  |
| oserdes_clk_3      | oserdes_clk_3      | DDR_INF_inst/u_mig_7series_0_mig/u_memc_ui_top_std/mem_intfc0/ddr_phy_top0/u_ddr_mc_phy_wrapper/u_ddr_mc_phy/ddr_phy_4lanes_0.u_ddr_phy_4lanes/ddr_byte_lane_D.ddr_byte_lane_D/ddr_byte_group_io/output_[6].oserdes_dq_.ddr.oserdes_dq_i/RST  |
| oserdes_clk_7      | oserdes_clk_7      | DDR_INF_inst/u_mig_7series_0_mig/u_memc_ui_top_std/mem_intfc0/ddr_phy_top0/u_ddr_mc_phy_wrapper/u_ddr_mc_phy/ddr_phy_4lanes_1.u_ddr_phy_4lanes/ddr_byte_lane_D.ddr_byte_lane_D/ddr_byte_group_io/output_[6].oserdes_dq_.sdr.oserdes_dq_i/RST  |
| oserdes_clk        | oserdes_clk        | DDR_INF_inst/u_mig_7series_0_mig/u_memc_ui_top_std/mem_intfc0/ddr_phy_top0/u_ddr_mc_phy_wrapper/u_ddr_mc_phy/ddr_phy_4lanes_0.u_ddr_phy_4lanes/ddr_byte_lane_A.ddr_byte_lane_A/ddr_byte_group_io/output_[9].oserdes_dq_.ddr.oserdes_dq_i/RST  |
| oserdes_clk_1      | oserdes_clk_1      | DDR_INF_inst/u_mig_7series_0_mig/u_memc_ui_top_std/mem_intfc0/ddr_phy_top0/u_ddr_mc_phy_wrapper/u_ddr_mc_phy/ddr_phy_4lanes_0.u_ddr_phy_4lanes/ddr_byte_lane_B.ddr_byte_lane_B/ddr_byte_group_io/output_[3].oserdes_dq_.ddr.oserdes_dq_i/RST  |
| oserdes_clk_6      | oserdes_clk_6      | DDR_INF_inst/u_mig_7series_0_mig/u_memc_ui_top_std/mem_intfc0/ddr_phy_top0/u_ddr_mc_phy_wrapper/u_ddr_mc_phy/ddr_phy_4lanes_1.u_ddr_phy_4lanes/ddr_byte_lane_C.ddr_byte_lane_C/ddr_byte_group_io/output_[11].oserdes_dq_.sdr.oserdes_dq_i/RST |
| oserdes_clk_3      | oserdes_clk_3      | DDR_INF_inst/u_mig_7series_0_mig/u_memc_ui_top_std/mem_intfc0/ddr_phy_top0/u_ddr_mc_phy_wrapper/u_ddr_mc_phy/ddr_phy_4lanes_0.u_ddr_phy_4lanes/ddr_byte_lane_D.ddr_byte_lane_D/ddr_byte_group_io/output_[8].oserdes_dq_.ddr.oserdes_dq_i/RST  |
| oserdes_clk_7      | oserdes_clk_7      | DDR_INF_inst/u_mig_7series_0_mig/u_memc_ui_top_std/mem_intfc0/ddr_phy_top0/u_ddr_mc_phy_wrapper/u_ddr_mc_phy/ddr_phy_4lanes_1.u_ddr_phy_4lanes/ddr_byte_lane_D.ddr_byte_lane_D/ddr_byte_group_io/output_[8].oserdes_dq_.sdr.oserdes_dq_i/RST  |
| oserdes_clk        | oserdes_clk        | DDR_INF_inst/u_mig_7series_0_mig/u_memc_ui_top_std/mem_intfc0/ddr_phy_top0/u_ddr_mc_phy_wrapper/u_ddr_mc_phy/ddr_phy_4lanes_0.u_ddr_phy_4lanes/ddr_byte_lane_A.ddr_byte_lane_A/ddr_byte_group_io/output_[5].oserdes_dq_.ddr.oserdes_dq_i/RST  |
| oserdes_clk_3      | oserdes_clk_3      | DDR_INF_inst/u_mig_7series_0_mig/u_memc_ui_top_std/mem_intfc0/ddr_phy_top0/u_ddr_mc_phy_wrapper/u_ddr_mc_phy/ddr_phy_4lanes_0.u_ddr_phy_4lanes/ddr_byte_lane_D.ddr_byte_lane_D/ddr_byte_group_io/output_[7].oserdes_dq_.ddr.oserdes_dq_i/RST  |
| oserdes_clk_7      | oserdes_clk_7      | DDR_INF_inst/u_mig_7series_0_mig/u_memc_ui_top_std/mem_intfc0/ddr_phy_top0/u_ddr_mc_phy_wrapper/u_ddr_mc_phy/ddr_phy_4lanes_1.u_ddr_phy_4lanes/ddr_byte_lane_D.ddr_byte_lane_D/ddr_byte_group_io/output_[7].oserdes_dq_.sdr.oserdes_dq_i/RST  |
| oserdes_clk_3      | oserdes_clk_3      | DDR_INF_inst/u_mig_7series_0_mig/u_memc_ui_top_std/mem_intfc0/ddr_phy_top0/u_ddr_mc_phy_wrapper/u_ddr_mc_phy/ddr_phy_4lanes_0.u_ddr_phy_4lanes/ddr_byte_lane_D.ddr_byte_lane_D/ddr_byte_group_io/output_[4].oserdes_dq_.ddr.oserdes_dq_i/RST  |
| oserdes_clk_7      | oserdes_clk_7      | DDR_INF_inst/u_mig_7series_0_mig/u_memc_ui_top_std/mem_intfc0/ddr_phy_top0/u_ddr_mc_phy_wrapper/u_ddr_mc_phy/ddr_phy_4lanes_1.u_ddr_phy_4lanes/ddr_byte_lane_D.ddr_byte_lane_D/ddr_byte_group_io/output_[4].oserdes_dq_.sdr.oserdes_dq_i/RST  |
| oserdes_clk        | oserdes_clk        | DDR_INF_inst/u_mig_7series_0_mig/u_memc_ui_top_std/mem_intfc0/ddr_phy_top0/u_ddr_mc_phy_wrapper/u_ddr_mc_phy/ddr_phy_4lanes_0.u_ddr_phy_4lanes/ddr_byte_lane_A.ddr_byte_lane_A/ddr_byte_group_io/output_[7].oserdes_dq_.ddr.oserdes_dq_i/RST  |
| oserdes_clk_4      | oserdes_clk_4      | DDR_INF_inst/u_mig_7series_0_mig/u_memc_ui_top_std/mem_intfc0/ddr_phy_top0/u_ddr_mc_phy_wrapper/u_ddr_mc_phy/ddr_phy_4lanes_1.u_ddr_phy_4lanes/ddr_byte_lane_A.ddr_byte_lane_A/ddr_byte_group_io/output_[1].oserdes_dq_.sdr.oserdes_dq_i/RST  |
| oserdes_clk        | oserdes_clk        | DDR_INF_inst/u_mig_7series_0_mig/u_memc_ui_top_std/mem_intfc0/ddr_phy_top0/u_ddr_mc_phy_wrapper/u_ddr_mc_phy/ddr_phy_4lanes_0.u_ddr_phy_4lanes/ddr_byte_lane_A.ddr_byte_lane_A/ddr_byte_group_io/output_[1].oserdes_dq_.ddr.oserdes_dq_i/RST  |
| oserdes_clk_1      | oserdes_clk_1      | DDR_INF_inst/u_mig_7series_0_mig/u_memc_ui_top_std/mem_intfc0/ddr_phy_top0/u_ddr_mc_phy_wrapper/u_ddr_mc_phy/ddr_phy_4lanes_0.u_ddr_phy_4lanes/ddr_byte_lane_B.ddr_byte_lane_B/ddr_byte_group_io/output_[2].oserdes_dq_.ddr.oserdes_dq_i/RST  |
| oserdes_clk_2      | oserdes_clk_2      | DDR_INF_inst/u_mig_7series_0_mig/u_memc_ui_top_std/mem_intfc0/ddr_phy_top0/u_ddr_mc_phy_wrapper/u_ddr_mc_phy/ddr_phy_4lanes_0.u_ddr_phy_4lanes/ddr_byte_lane_C.ddr_byte_lane_C/ddr_byte_group_io/output_[6].oserdes_dq_.ddr.oserdes_dq_i/RST  |
| oserdes_clk_4      | oserdes_clk_4      | DDR_INF_inst/u_mig_7series_0_mig/u_memc_ui_top_std/mem_intfc0/ddr_phy_top0/u_ddr_mc_phy_wrapper/u_ddr_mc_phy/ddr_phy_4lanes_1.u_ddr_phy_4lanes/ddr_byte_lane_A.ddr_byte_lane_A/ddr_byte_group_io/output_[0].oserdes_dq_.sdr.oserdes_dq_i/RST  |
| oserdes_clk        | oserdes_clk        | DDR_INF_inst/u_mig_7series_0_mig/u_memc_ui_top_std/mem_intfc0/ddr_phy_top0/u_ddr_mc_phy_wrapper/u_ddr_mc_phy/ddr_phy_4lanes_0.u_ddr_phy_4lanes/ddr_byte_lane_A.ddr_byte_lane_A/ddr_byte_group_io/output_[0].oserdes_dq_.ddr.oserdes_dq_i/RST  |
| oserdes_clk_3      | oserdes_clk_3      | DDR_INF_inst/u_mig_7series_0_mig/u_memc_ui_top_std/mem_intfc0/ddr_phy_top0/u_ddr_mc_phy_wrapper/u_ddr_mc_phy/ddr_phy_4lanes_0.u_ddr_phy_4lanes/ddr_byte_lane_D.ddr_byte_lane_D/ddr_byte_group_io/output_[9].oserdes_dq_.ddr.oserdes_dq_i/RST  |
| oserdes_clk_1      | oserdes_clk_1      | DDR_INF_inst/u_mig_7series_0_mig/u_memc_ui_top_std/mem_intfc0/ddr_phy_top0/u_ddr_mc_phy_wrapper/u_ddr_mc_phy/ddr_phy_4lanes_0.u_ddr_phy_4lanes/ddr_byte_lane_B.ddr_byte_lane_B/ddr_byte_group_io/output_[4].oserdes_dq_.ddr.oserdes_dq_i/RST  |
| oserdes_clk_6      | oserdes_clk_6      | DDR_INF_inst/u_mig_7series_0_mig/u_memc_ui_top_std/mem_intfc0/ddr_phy_top0/u_ddr_mc_phy_wrapper/u_ddr_mc_phy/ddr_phy_4lanes_1.u_ddr_phy_4lanes/ddr_byte_lane_C.ddr_byte_lane_C/ddr_byte_group_io/output_[6].oserdes_dq_.sdr.oserdes_dq_i/RST  |
| oserdes_clk_7      | oserdes_clk_7      | DDR_INF_inst/u_mig_7series_0_mig/u_memc_ui_top_std/mem_intfc0/ddr_phy_top0/u_ddr_mc_phy_wrapper/u_ddr_mc_phy/ddr_phy_4lanes_1.u_ddr_phy_4lanes/ddr_byte_lane_D.ddr_byte_lane_D/ddr_byte_group_io/output_[9].oserdes_dq_.sdr.oserdes_dq_i/RST  |
| oserdes_clk_5      | oserdes_clk_5      | DDR_INF_inst/u_mig_7series_0_mig/u_memc_ui_top_std/mem_intfc0/ddr_phy_top0/u_ddr_mc_phy_wrapper/u_ddr_mc_phy/ddr_phy_4lanes_1.u_ddr_phy_4lanes/ddr_byte_lane_B.ddr_byte_lane_B/ddr_byte_group_io/output_[4].oserdes_dq_.sdr.oserdes_dq_i/RST  |
| oserdes_clk        | oserdes_clk        | DDR_INF_inst/u_mig_7series_0_mig/u_memc_ui_top_std/mem_intfc0/ddr_phy_top0/u_ddr_mc_phy_wrapper/u_ddr_mc_phy/ddr_phy_4lanes_0.u_ddr_phy_4lanes/ddr_byte_lane_A.ddr_byte_lane_A/ddr_byte_group_io/output_[3].oserdes_dq_.ddr.oserdes_dq_i/RST  |
| oserdes_clk_3      | oserdes_clk_3      | DDR_INF_inst/u_mig_7series_0_mig/u_memc_ui_top_std/mem_intfc0/ddr_phy_top0/u_ddr_mc_phy_wrapper/u_ddr_mc_phy/ddr_phy_4lanes_0.u_ddr_phy_4lanes/ddr_byte_lane_D.ddr_byte_lane_D/ddr_byte_group_io/output_[5].oserdes_dq_.ddr.oserdes_dq_i/RST  |
| oserdes_clk_7      | oserdes_clk_7      | DDR_INF_inst/u_mig_7series_0_mig/u_memc_ui_top_std/mem_intfc0/ddr_phy_top0/u_ddr_mc_phy_wrapper/u_ddr_mc_phy/ddr_phy_4lanes_1.u_ddr_phy_4lanes/ddr_byte_lane_D.ddr_byte_lane_D/ddr_byte_group_io/output_[5].oserdes_dq_.sdr.oserdes_dq_i/RST  |
| clk_pll_i          | clk_pll_i          | DDR_INF_inst/u_mig_7series_0_mig/u_memc_ui_top_std/mem_intfc0/mc0/bank_mach0/arb_mux0/arb_row_col0/rnk_config_strobe_r_reg[0]/D                                                                                                               |
| clk_pll_i          | clk_pll_i          | DDR_INF_inst/u_mig_7series_0_mig/u_memc_ui_top_std/mem_intfc0/ddr_phy_top0/u_ddr_calib_top/oclk_calib.u_ddr_phy_oclkdelay_cal/u_ocd_mux/po_setup_r_reg[0]/D                                                                                   |
| clk_pll_i          | clk_pll_i          | DDR_INF_inst/u_mig_7series_0_mig/u_memc_ui_top_std/mem_intfc0/ddr_phy_top0/u_ddr_calib_top/oclk_calib.u_ddr_phy_oclkdelay_cal/u_ocd_mux/po_stg23_incdec_r_reg/D                                                                               |
| clk_pll_i          | clk_pll_i          | DDR_INF_inst/u_mig_7series_0_mig/u_memc_ui_top_std/mem_intfc0/ddr_phy_top0/u_ddr_calib_top/oclk_calib.u_ddr_phy_oclkdelay_cal/u_ocd_mux/po_setup_r_reg[1]/D                                                                                   |
| clk_5x_pre         | clk_5x_pre         | Inst_dvid/ODDR2_green/D1                                                                                                                                                                                                                      |
| clk_5x_pre         | clk_5x_pre         | Inst_dvid/ODDR2_green/D2                                                                                                                                                                                                                      |
| clk_5x_pre         | clk_5x_pre         | Inst_dvid/shift_clock_reg[0]/D                                                                                                                                                                                                                |
| clk_pll_i          | clk_pll_i          | DDR_INF_inst/u_mig_7series_0_mig/u_memc_ui_top_std/mem_intfc0/mc0/bank_mach0/arb_mux0/arb_row_col0/col_arb0/grant_r_reg[1]/D                                                                                                                  |
+--------------------+--------------------+-----------------------------------------------------------------------------------------------------------------------------------------------------------------------------------------------------------------------------------------------+

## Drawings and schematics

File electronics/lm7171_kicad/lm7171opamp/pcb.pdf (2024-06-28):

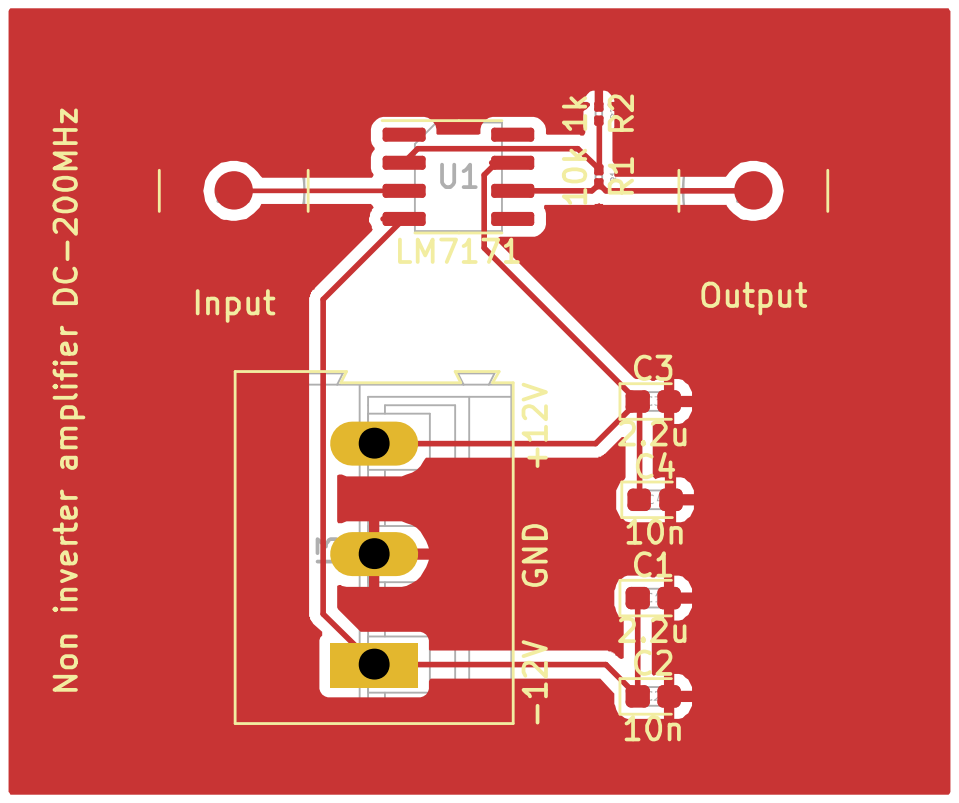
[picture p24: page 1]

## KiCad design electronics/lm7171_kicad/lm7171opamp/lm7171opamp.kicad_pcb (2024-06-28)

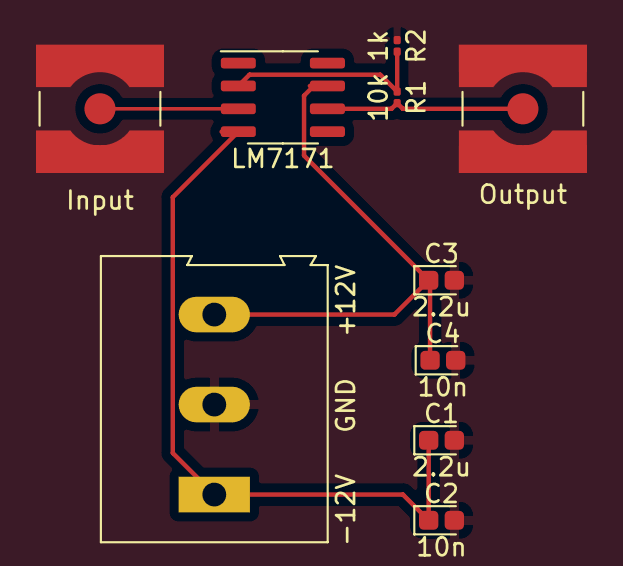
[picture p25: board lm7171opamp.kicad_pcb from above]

Board: 2 copper layers, 10 parts (0 on the bottom side), 6 nets.

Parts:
C1, C3: 2.2u; CP_EIA-1608-08_AVX-J
C2, C4: 10n; CP_EIA-1608-08_AVX-J
J1: Input; SMA_Amphenol_132134-10_Vertical
J2: Output; SMA_Amphenol_132134-10_Vertical
J3: -12V GND +12V; TerminalBlock_Altech_AK300-3_P5.00mm
R1: 10k; R_0201_0603Metric
R2: 1k; R_0201_0603Metric
U1: LM7171; SOIC-8_3.9x4.9mm_P1.27mm

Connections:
GND: C1.2, C2.2, C3.2, C4.2, J1.2 (Ext), J2.2 (Ext), J3.2, R2.1
unnamed: J1.1 (In), U1.3 (+)
unnamed: J2.1 (In), R1.2, U1.6
unnamed: C1.1, C2.1, J3.1, U1.4 (V-)
unnamed: C3.1, C4.1, J3.3, U1.7 (V+)
unnamed: R1.1, R2.2, U1.2 (-)

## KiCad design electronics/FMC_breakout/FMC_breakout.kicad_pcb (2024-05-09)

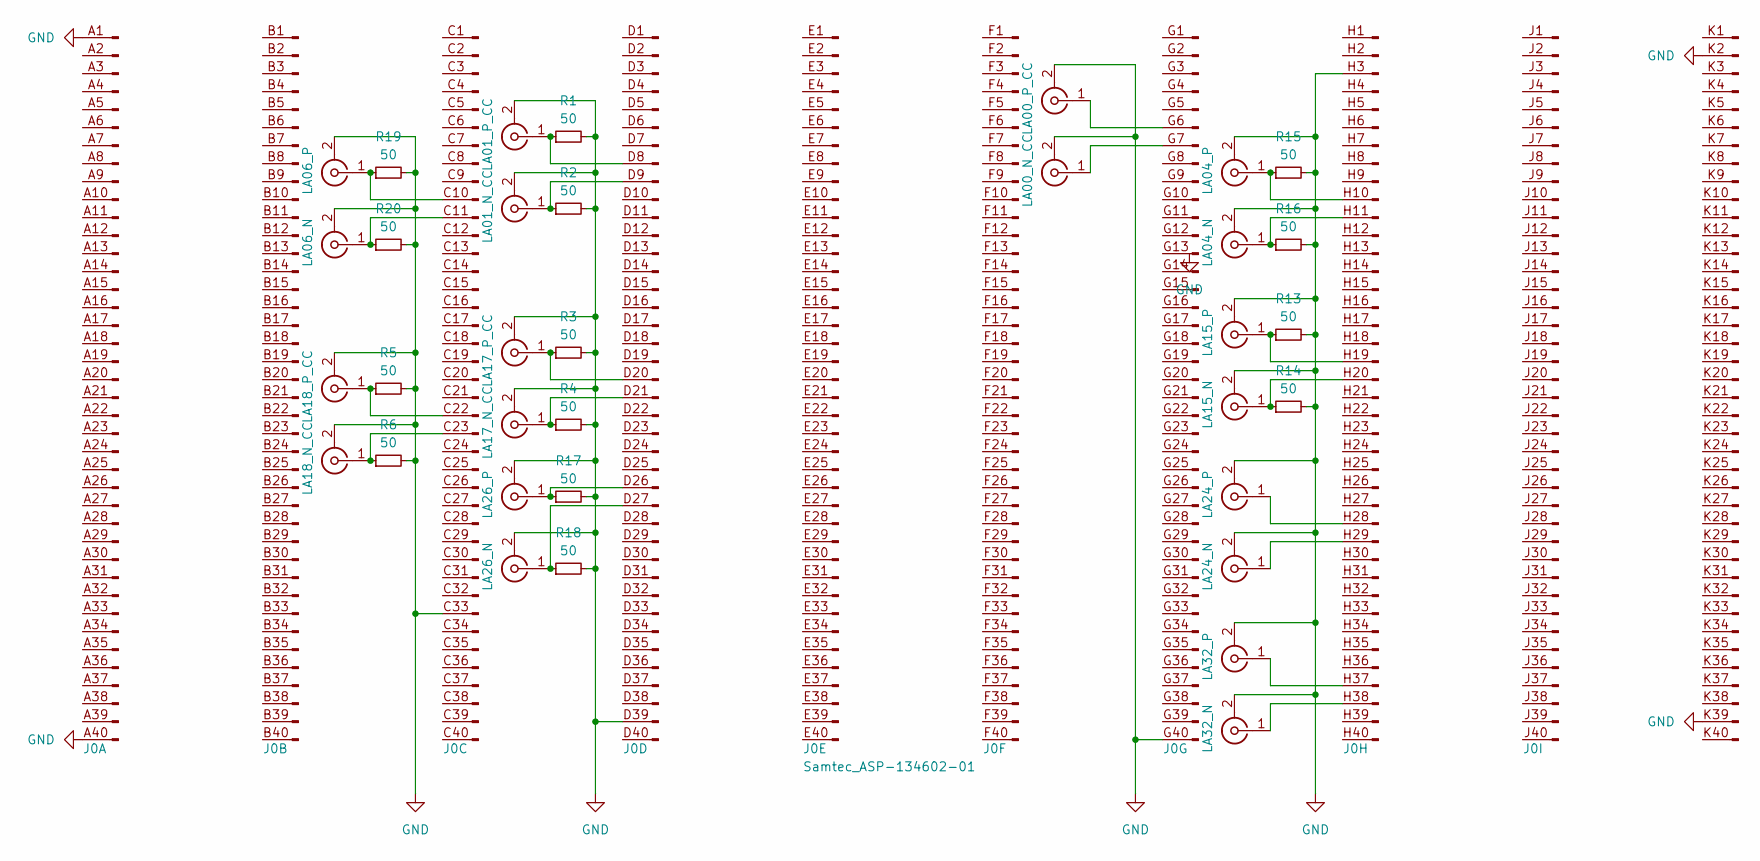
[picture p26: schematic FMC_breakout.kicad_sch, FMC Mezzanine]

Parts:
J0: Samtec_ASP-134602-01; Samtec_FMC_ASP-134602-01_10x40_P1.27mm_Vertical; LCSC C2875619
J1: LA01_P_CC; U.FL_Hirose_U.FL-R-SMT-1_Vertical
J2: LA01_N_CC; U.FL_Hirose_U.FL-R-SMT-1_Vertical
J3: LA17_P_CC; U.FL_Hirose_U.FL-R-SMT-1_Vertical
J4: LA17_N_CC; U.FL_Hirose_U.FL-R-SMT-1_Vertical
J5: LA18_P_CC; U.FL_Hirose_U.FL-R-SMT-1_Vertical
J6: LA18_N_CC; U.FL_Hirose_U.FL-R-SMT-1_Vertical
J7: LA00_P_CC; U.FL_Hirose_U.FL-R-SMT-1_Vertical
J8: LA00_N_CC; U.FL_Hirose_U.FL-R-SMT-1_Vertical
J9: LA32_P; U.FL_Hirose_U.FL-R-SMT-1_Vertical
J10: LA32_N; U.FL_Hirose_U.FL-R-SMT-1_Vertical
J11: LA24_P; U.FL_Hirose_U.FL-R-SMT-1_Vertical
J12: LA24_N; U.FL_Hirose_U.FL-R-SMT-1_Vertical
J13: LA15_P; U.FL_Hirose_U.FL-R-SMT-1_Vertical
J14: LA15_N; U.FL_Hirose_U.FL-R-SMT-1_Vertical
J15: LA04_P; U.FL_Hirose_U.FL-R-SMT-1_Vertical
J16: LA04_N; U.FL_Hirose_U.FL-R-SMT-1_Vertical
J17: LA26_P; U.FL_Hirose_U.FL-R-SMT-1_Vertical
J18: LA26_N; U.FL_Hirose_U.FL-R-SMT-1_Vertical
J19: LA06_P; U.FL_Hirose_U.FL-R-SMT-1_Vertical; LCSC C434812
J20: LA06_N; U.FL_Hirose_U.FL-R-SMT-1_Vertical
R1, R2, R3, R4, R5, R6, R13, R14, R15, R16, R17, R19, R20: 50; R_0402_1005Metric
R18: 50; R_0402_1005Metric; LCSC C853312

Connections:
GND: J0.A1 (Pin_1), J0.A40 (Pin_40), J0.C33 (Pin_33), J0.D39 (Pin_39), J0.G40 (Pin_40), J0.H3 (Pin_3), J0.K2 (Pin_2), J0.K39 (Pin_39), J1.2 (Ext), J2.2 (Ext), J3.2 (Ext), J4.2 (Ext), J5.2 (Ext), J6.2 (Ext), J7.2 (Ext), J8.2 (Ext), J9.2 (Ext), J10.2 (Ext), J11.2 (Ext), J12.2 (Ext), J13.2 (Ext), J14.2 (Ext), J15.2 (Ext), J16.2 (Ext), J17.2 (Ext), J18.2 (Ext), J19.2 (Ext), J20.2 (Ext), R1.2, R2.2, R3.2, R4.2, R5.2, R6.2, R13.2, R14.2, R15.2, R16.2, R17.2, R18.2, R19.2, R20.2
unnamed: J0.C10 (Pin_10), J19.1 (In), R19.1
unnamed: J0.C11 (Pin_11), J20.1 (In), R20.1
unnamed: J0.C22 (Pin_22), J5.1 (In), R5.1
unnamed: J0.C23 (Pin_23), J6.1 (In), R6.1
unnamed: J0.D8 (Pin_8), J1.1 (In), R1.1
unnamed: J0.D9 (Pin_9), J2.1 (In), R2.1
unnamed: J0.D20 (Pin_20), J3.1 (In), R3.1
unnamed: J0.D21 (Pin_21), J4.1 (In), R4.1
unnamed: J0.D26 (Pin_26), J17.1 (In), R17.1
unnamed: J0.D27 (Pin_27), J18.1 (In), R18.1
unnamed: J0.G6 (Pin_6), J7.1 (In)
unnamed: J0.G7 (Pin_7), J8.1 (In)
unnamed: J0.H10 (Pin_10), J15.1 (In), R15.1
unnamed: J0.H11 (Pin_11), J16.1 (In), R16.1
unnamed: J0.H19 (Pin_19), J13.1 (In), R13.1
unnamed: J0.H20 (Pin_20), J14.1 (In), R14.1
unnamed: J0.H28 (Pin_28), J11.1 (In)
unnamed: J0.H29 (Pin_29), J12.1 (In)
unnamed: J0.H37 (Pin_37), J9.1 (In)
unnamed: J0.H38 (Pin_38), J10.1 (In)

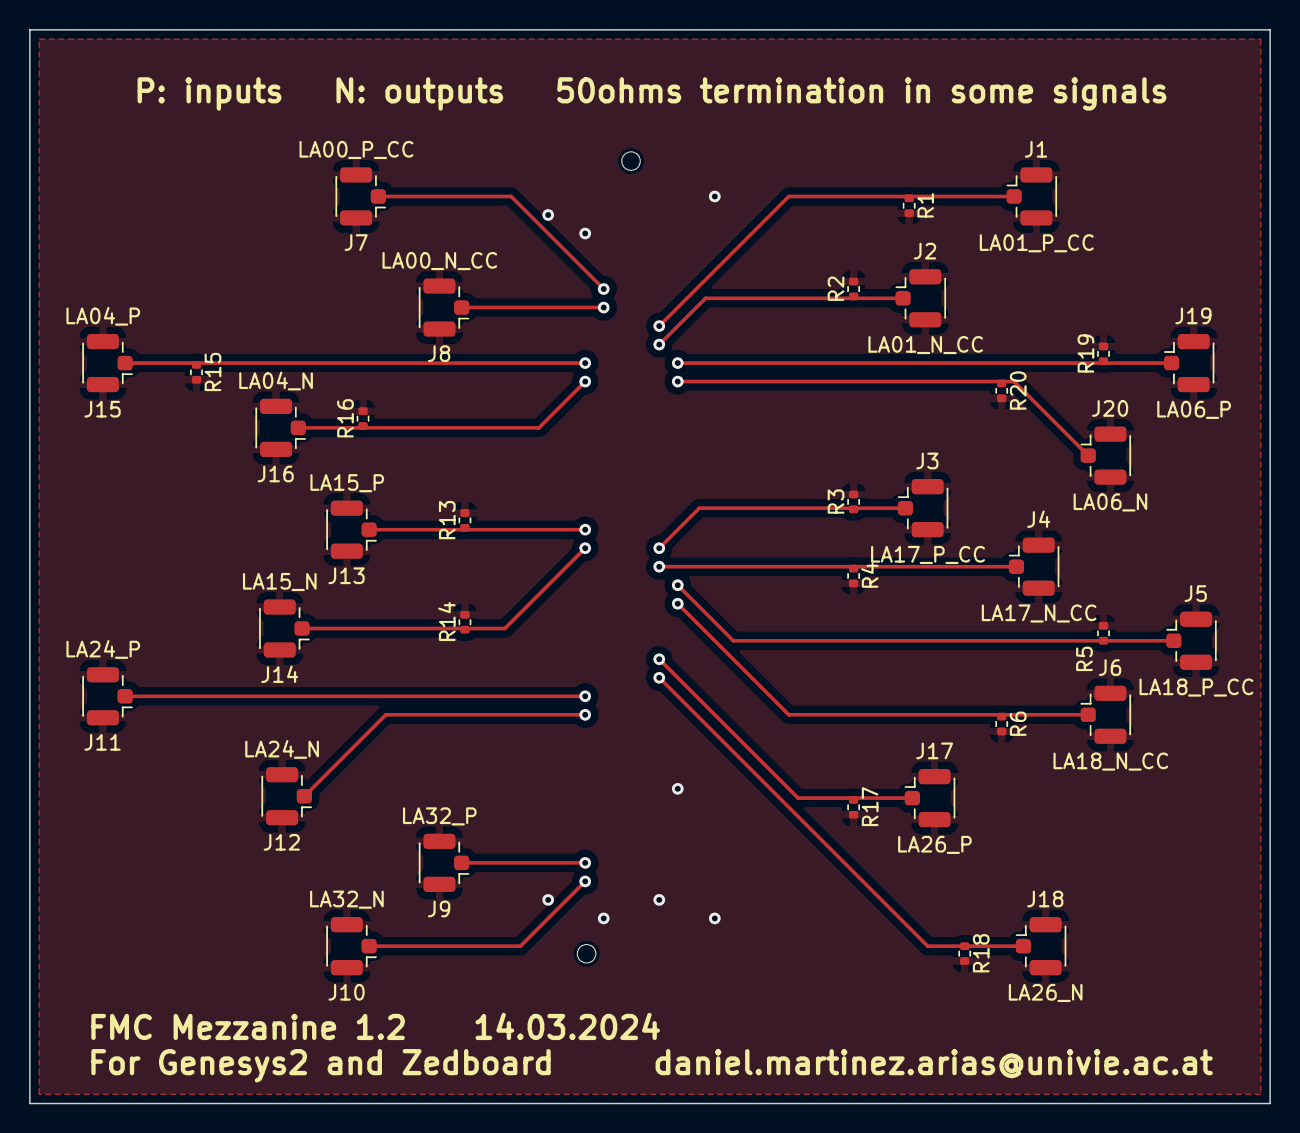
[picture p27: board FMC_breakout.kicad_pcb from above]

Board: 2 copper layers, 85.1 x 73.7 mm, 35 parts (1 on the bottom side), 21 nets.

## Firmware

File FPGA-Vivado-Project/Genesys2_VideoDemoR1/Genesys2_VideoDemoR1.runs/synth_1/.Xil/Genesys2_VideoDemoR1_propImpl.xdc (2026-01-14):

set_property SRC_FILE_INFO {cfile:C:/Users/crist/OneDrive/Documentos/GitHub/FPGA-UBB-project/FPGA-Vivado-Project/srcs/Genesys-2_Video.xdc rfile:../../../../srcs/Genesys-2_Video.xdc id:1} [current_design]
set_property SRC_FILE_INFO {cfile:C:/Users/crist/OneDrive/Documentos/GitHub/FPGA-UBB-project/FPGA-Vivado-Project/srcs/timing.xdc rfile:../../../../srcs/timing.xdc id:2} [current_design]
set_property src_info {type:XDC file:1 line:7 export:INPUT save:INPUT read:READ} [current_design]
set_property -dict {PACKAGE_PIN AD11 IOSTANDARD LVDS} [get_ports sysclk_n]
set_property src_info {type:XDC file:1 line:8 export:INPUT save:INPUT read:READ} [current_design]
set_property -dict {PACKAGE_PIN AD12 IOSTANDARD LVDS} [get_ports sysclk_p]
set_property src_info {type:XDC file:1 line:16 export:INPUT save:INPUT read:READ} [current_design]
set_property -dict {PACKAGE_PIN R19 IOSTANDARD LVCMOS33} [get_ports cpu_resetn]
set_property src_info {type:XDC file:1 line:19 export:INPUT save:INPUT read:READ} [current_design]
set_property -dict {PACKAGE_PIN T28 IOSTANDARD LVCMOS33} [get_ports {led[0]}]
set_property src_info {type:XDC file:1 line:20 export:INPUT save:INPUT read:READ} [current_design]
set_property -dict {PACKAGE_PIN V19 IOSTANDARD LVCMOS33} [get_ports {led[1]}]
set_property src_info {type:XDC file:1 line:21 export:INPUT save:INPUT read:READ} [current_design]
set_property -dict {PACKAGE_PIN U30 IOSTANDARD LVCMOS33} [get_ports {led[2]}]
set_property src_info {type:XDC file:1 line:22 export:INPUT save:INPUT read:READ} [current_design]
set_property -dict {PACKAGE_PIN U29 IOSTANDARD LVCMOS33} [get_ports {led[3]}]
set_property src_info {type:XDC file:1 line:23 export:INPUT save:INPUT read:READ} [current_design]
set_property -dict {PACKAGE_PIN V20 IOSTANDARD LVCMOS33} [get_ports {led[4]}]
set_property src_info {type:XDC file:1 line:24 export:INPUT save:INPUT read:READ} [current_design]
set_property -dict {PACKAGE_PIN V26 IOSTANDARD LVCMOS33} [get_ports {led[5]}]
set_property src_info {type:XDC file:1 line:25 export:INPUT save:INPUT read:READ} [current_design]
set_property -dict {PACKAGE_PIN W24 IOSTANDARD LVCMOS33} [get_ports {led[6]}]
set_property src_info {type:XDC file:1 line:26 export:INPUT save:INPUT read:READ} [current_design]
set_property -dict {PACKAGE_PIN W23 IOSTANDARD LVCMOS33} [get_ports {led[7]}]
set_property src_info {type:XDC file:1 line:43 export:INPUT save:INPUT read:READ} [current_design]
set_property -dict {PACKAGE_PIN Y23 IOSTANDARD LVCMOS33} [get_ports uart_rx_out]
set_property src_info {type:XDC file:1 line:44 export:INPUT save:INPUT read:READ} [current_design]
set_property -dict {PACKAGE_PIN Y20 IOSTANDARD LVCMOS33} [get_ports uart_tx_in]
set_property src_info {type:XDC file:1 line:125 export:INPUT save:INPUT read:READ} [current_design]
set_property -dict {PACKAGE_PIN AB20 IOSTANDARD TMDS_33} [get_ports hdmi_tx_clk_n]
set_property src_info {type:XDC file:1 line:126 export:INPUT save:INPUT read:READ} [current_design]
set_property -dict {PACKAGE_PIN AA20 IOSTANDARD TMDS_33} [get_ports hdmi_tx_clk_p]
set_property src_info {type:XDC file:1 line:130 export:INPUT save:INPUT read:READ} [current_design]
set_property -dict {PACKAGE_PIN AC21 IOSTANDARD TMDS_33} [get_ports {hdmi_tx_n[0]}]
set_property src_info {type:XDC file:1 line:131 export:INPUT save:INPUT read:READ} [current_design]
set_property -dict {PACKAGE_PIN AC20 IOSTANDARD TMDS_33} [get_ports {hdmi_tx_p[0]}]
set_property src_info {type:XDC file:1 line:132 export:INPUT save:INPUT read:READ} [current_design]
set_property -dict {PACKAGE_PIN AA23 IOSTANDARD TMDS_33} [get_ports {hdmi_tx_n[1]}]
set_property src_info {type:XDC file:1 line:133 export:INPUT save:INPUT read:READ} [current_design]
set_property -dict {PACKAGE_PIN AA22 IOSTANDARD TMDS_33} [get_ports {hdmi_tx_p[1]}]
set_property src_info {type:XDC file:1 line:134 export:INPUT save:INPUT read:READ} [current_design]
set_property -dict {PACKAGE_PIN AC25 IOSTANDARD TMDS_33} [get_ports {hdmi_tx_n[2]}]
set_property src_info {type:XDC file:1 line:135 export:INPUT save:INPUT read:READ} [current_design]
set_property -dict {PACKAGE_PIN AB24 IOSTANDARD TMDS_33} [get_ports {hdmi_tx_p[2]}]
set_property src_info {type:XDC file:1 line:166 export:INPUT save:INPUT read:READ} [current_design]
set_property -dict { PACKAGE_PIN AC26  IOSTANDARD LVCMOS33 } [get_ports { jc[0] }]; #IO_L19P_T3_13 Sch=jc[1]
set_property src_info {type:XDC file:1 line:167 export:INPUT save:INPUT read:READ} [current_design]
set_property -dict { PACKAGE_PIN AJ27  IOSTANDARD LVCMOS33 } [get_ports { jc[1] }]; #IO_L20P_T3_13 Sch=jc[2]
set_property src_info {type:XDC file:1 line:168 export:INPUT save:INPUT read:READ} [current_design]
set_property -dict { PACKAGE_PIN AH30  IOSTANDARD LVCMOS33 } [get_ports { jc[2] }]; #IO_L18N_T2_13 Sch=jc[3]
set_property src_info {type:XDC file:1 line:169 export:INPUT save:INPUT read:READ} [current_design]
set_property -dict { PACKAGE_PIN AK29  IOSTANDARD LVCMOS33 } [get_ports { jc[3] }]; #IO_L15P_T2_DQS_13 Sch=jc[4]
set_property src_info {type:XDC file:1 line:170 export:INPUT save:INPUT read:READ} [current_design]
set_property -dict { PACKAGE_PIN AD26  IOSTANDARD LVCMOS33 } [get_ports { jc[4] }]; #IO_L19N_T3_VREF_13 Sch=jc[7]
set_property src_info {type:XDC file:1 line:171 export:INPUT save:INPUT read:READ} [current_design]
set_property -dict { PACKAGE_PIN AG30  IOSTANDARD LVCMOS33 } [get_ports { jc[5] }]; #IO_L18P_T2_13 Sch=jc[8]
set_property src_info {type:XDC file:1 line:172 export:INPUT save:INPUT read:READ} [current_design]
set_property -dict { PACKAGE_PIN AK30  IOSTANDARD LVCMOS33 } [get_ports { jc[6] }]; #IO_L15N_T2_DQS_13 Sch=jc[9]
set_property src_info {type:XDC file:1 line:173 export:INPUT save:INPUT read:READ} [current_design]
set_property -dict { PACKAGE_PIN AK28  IOSTANDARD LVCMOS33 } [get_ports { jc[7] }]; #IO_L20N_T3_13 Sch=jc[10]
set_property src_info {type:XDC file:1 line:295 export:INPUT save:INPUT read:READ} [current_design]
set_property -dict { PACKAGE_PIN C27   IOSTANDARD LVCMOS33 } [get_ports { fmc_la_n_00 }]; #IO_L13N_T2_MRCC_16 Sch=fmc_la_n[00]
set_property src_info {type:XDC file:1 line:296 export:INPUT save:INPUT read:READ} [current_design]
set_property -dict { PACKAGE_PIN D27   IOSTANDARD LVCMOS33 } [get_ports { fmc_la_p_00 }]; #IO_L13P_T2_MRCC_16 Sch=fmc_la_p[00]
set_property src_info {type:XDC file:1 line:298 export:INPUT save:INPUT read:READ} [current_design]
set_property -dict { PACKAGE_PIN D26   IOSTANDARD LVCMOS33 } [get_ports { fmc_la_p_01 }]; #IO_L11P_T1_SRCC_16 Sch=fmc_la_p[01]
set_property src_info {type:XDC file:1 line:303 export:INPUT save:INPUT read:READ} [current_design]
set_property -dict { PACKAGE_PIN H27   IOSTANDARD LVCMOS33 } [get_ports { fmc_la_n_04 }]; #IO_L23N_T3_16 Sch=fmc_la_n[04]
set_property src_info {type:XDC file:1 line:304 export:INPUT save:INPUT read:READ} [current_design]
set_property -dict { PACKAGE_PIN H26   IOSTANDARD LVCMOS33 } [get_ports { fmc_la_p_04 }]; #IO_L23P_T3_16 Sch=fmc_la_p[04]
set_property src_info {type:XDC file:1 line:308 export:INPUT save:INPUT read:READ} [current_design]
set_property -dict { PACKAGE_PIN D29   IOSTANDARD LVCMOS33 } [get_ports { fmc_la_p_06 }]; #IO_L16P_T2_16 Sch=fmc_la_p[06]
set_property src_info {type:XDC file:1 line:326 export:INPUT save:INPUT read:READ} [current_design]
set_property -dict { PACKAGE_PIN B23   IOSTANDARD LVCMOS33 } [get_ports { fmc_la_p_15 }]; #IO_L1P_T0_16 Sch=fmc_la_p[15]
set_property src_info {type:XDC file:1 line:329 export:INPUT save:INPUT read:READ} [current_design]
set_property -dict { PACKAGE_PIN E21   IOSTANDARD LVCMOS33 } [get_ports { fmc_la_n_17 }]; #IO_L11N_T1_SRCC_17 Sch=fmc_la_n[17]
set_property src_info {type:XDC file:1 line:330 export:INPUT save:INPUT read:READ} [current_design]
set_property -dict { PACKAGE_PIN F21   IOSTANDARD LVCMOS33 } [get_ports { fmc_la_p_17 }]; #IO_L11P_T1_SRCC_17 Sch=fmc_la_p[17]
set_property src_info {type:XDC file:1 line:331 export:INPUT save:INPUT read:READ} [current_design]
set_property -dict { PACKAGE_PIN D18   IOSTANDARD LVCMOS33 } [get_ports { fmc_la_n_18 }]; #IO_L13N_T2_MRCC_17 Sch=fmc_la_n[18]
set_property src_info {type:XDC file:1 line:332 export:INPUT save:INPUT read:READ} [current_design]
set_property -dict { PACKAGE_PIN D17   IOSTANDARD LVCMOS33 } [get_ports { fmc_la_p_18 }]; #IO_L13P_T2_MRCC_17 Sch=fmc_la_p[18]
set_property src_info {type:XDC file:1 line:343 export:INPUT save:INPUT read:READ} [current_design]
set_property -dict { PACKAGE_PIN G20   IOSTANDARD LVCMOS33 } [get_ports { fmc_la_n_24 }]; #IO_L2N_T0_17 Sch=fmc_la_n[24]
set_property src_info {type:XDC file:1 line:344 export:INPUT save:INPUT read:READ} [current_design]
set_property -dict { PACKAGE_PIN H20   IOSTANDARD LVCMOS33 } [get_ports { fmc_la_p_24 }]; #IO_L2P_T0_17 Sch=fmc_la_p[24]
set_property src_info {type:XDC file:1 line:348 export:INPUT save:INPUT read:READ} [current_design]
set_property -dict { PACKAGE_PIN B22   IOSTANDARD LVCMOS33 } [get_ports { fmc_la_p_26 }]; #IO_L23P_T3_17 Sch=fmc_la_p[26]
set_property src_info {type:XDC file:1 line:359 export:INPUT save:INPUT read:READ} [current_design]
set_property -dict { PACKAGE_PIN J18   IOSTANDARD LVCMOS33 } [get_ports { fmc_la_n_32 }]; #IO_L1N_T0_17 Sch=fmc_la_n[32]
set_property src_info {type:XDC file:1 line:360 export:INPUT save:INPUT read:READ} [current_design]
set_property -dict { PACKAGE_PIN K18   IOSTANDARD LVCMOS33 } [get_ports { fmc_la_p_32 }]; #IO_L1P_T0_17 Sch=fmc_la_p[32]
set_property src_info {type:XDC file:1 line:372 export:INPUT save:INPUT read:READ} [current_design]
set_property -dict {PACKAGE_PIN AB27 IOSTANDARD LVCMOS33} [get_ports prog_clko]
set_property src_info {type:XDC file:1 line:373 export:INPUT save:INPUT read:READ} [current_design]
set_property -dict {PACKAGE_PIN AD27 IOSTANDARD LVCMOS33} [get_ports {prog_d[0]}]
set_property src_info {type:XDC file:1 line:374 export:INPUT save:INPUT read:READ} [current_design]
set_property -dict {PACKAGE_PIN W27 IOSTANDARD LVCMOS33} [get_ports {prog_d[1]}]
set_property src_info {type:XDC file:1 line:375 export:INPUT save:INPUT read:READ} [current_design]
set_property -dict {PACKAGE_PIN W28 IOSTANDARD LVCMOS33} [get_ports {prog_d[2]}]
set_property src_info {type:XDC file:1 line:376 export:INPUT save:INPUT read:READ} [current_design]
set_property -dict {PACKAGE_PIN W29 IOSTANDARD LVCMOS33} [get_ports {prog_d[3]}]
set_property src_info {type:XDC file:1 line:377 export:INPUT save:INPUT read:READ} [current_design]
set_property -dict {PACKAGE_PIN Y29 IOSTANDARD LVCMOS33} [get_ports {prog_d[4]}]
set_property src_info {type:XDC file:1 line:378 export:INPUT save:INPUT read:READ} [current_design]
set_property -dict {PACKAGE_PIN Y28 IOSTANDARD LVCMOS33} [get_ports {prog_d[5]}]
set_property src_info {type:XDC file:1 line:379 export:INPUT save:INPUT read:READ} [current_design]
set_property -dict {PACKAGE_PIN AA28 IOSTANDARD LVCMOS33} [get_ports {prog_d[6]}]
set_property src_info {type:XDC file:1 line:380 export:INPUT save:INPUT read:READ} [current_design]
set_property -dict {PACKAGE_PIN AA26 IOSTANDARD LVCMOS33} [get_ports {prog_d[7]}]
set_property src_info {type:XDC file:1 line:381 export:INPUT save:INPUT read:READ} [current_design]
set_property -dict {PACKAGE_PIN AC30 IOSTANDARD LVCMOS33} [get_ports prog_oen]
set_property src_info {type:XDC file:1 line:382 export:INPUT save:INPUT read:READ} [current_design]
set_property -dict {PACKAGE_PIN AB25 IOSTANDARD LVCMOS33} [get_ports prog_rdn]
set_property src_info {type:XDC file:1 line:383 export:INPUT save:INPUT read:READ} [current_design]
set_property -dict {PACKAGE_PIN AB29  IOSTANDARD LVCMOS33 } [get_ports prog_rxen]; #IO_L10P_T1_13 Sch=prog_rxfn
set_property src_info {type:XDC file:1 line:384 export:INPUT save:INPUT read:READ} [current_design]
set_property -dict {PACKAGE_PIN AB28 IOSTANDARD LVCMOS33} [get_ports prog_siwun]
set_property src_info {type:XDC file:1 line:385 export:INPUT save:INPUT read:READ} [current_design]
set_property -dict {PACKAGE_PIN AD29 IOSTANDARD LVCMOS33} [get_ports prog_spien]
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

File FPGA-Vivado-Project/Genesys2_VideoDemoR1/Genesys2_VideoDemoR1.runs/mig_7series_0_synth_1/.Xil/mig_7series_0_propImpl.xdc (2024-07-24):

set_property SRC_FILE_INFO {cfile:c:/Users/crist/OneDrive/Documentos/GitHub/FPGA-UBB-project/FPGA-Vivado-Project/Genesys2_VideoDemoR1/Genesys2_VideoDemoR1.gen/sources_1/ip/mig_7series_0/mig_7series_0/user_design/constraints/mig_7series_0.xdc rfile:../../../Genesys2_VideoDemoR1.gen/sources_1/ip/mig_7series_0/mig_7series_0/user_design/constraints/mig_7series_0.xdc id:1 order:EARLY} [current_design]
set_property src_info {type:XDC file:1 line:39 export:INPUT save:INPUT read:READ} [current_design]
set_property PACKAGE_PIN AD3 [get_ports {ddr3_dq[0]}]
set_property src_info {type:XDC file:1 line:45 export:INPUT save:INPUT read:READ} [current_design]
set_property PACKAGE_PIN AC2 [get_ports {ddr3_dq[1]}]
set_property src_info {type:XDC file:1 line:51 export:INPUT save:INPUT read:READ} [current_design]
set_property PACKAGE_PIN AC1 [get_ports {ddr3_dq[2]}]
set_property src_info {type:XDC file:1 line:57 export:INPUT save:INPUT read:READ} [current_design]
set_property PACKAGE_PIN AC5 [get_ports {ddr3_dq[3]}]
set_property src_info {type:XDC file:1 line:63 export:INPUT save:INPUT read:READ} [current_design]
set_property PACKAGE_PIN AC4 [get_ports {ddr3_dq[4]}]
set_property src_info {type:XDC file:1 line:69 export:INPUT save:INPUT read:READ} [current_design]
set_property PACKAGE_PIN AD6 [get_ports {ddr3_dq[5]}]
set_property src_info {type:XDC file:1 line:75 export:INPUT save:INPUT read:READ} [current_design]
set_property PACKAGE_PIN AE6 [get_ports {ddr3_dq[6]}]
set_property src_info {type:XDC file:1 line:81 export:INPUT save:INPUT read:READ} [current_design]
set_property PACKAGE_PIN AC7 [get_ports {ddr3_dq[7]}]
set_property src_info {type:XDC file:1 line:87 export:INPUT save:INPUT read:READ} [current_design]
set_property PACKAGE_PIN AF2 [get_ports {ddr3_dq[8]}]
set_property src_info {type:XDC file:1 line:93 export:INPUT save:INPUT read:READ} [current_design]
set_property PACKAGE_PIN AE1 [get_ports {ddr3_dq[9]}]
set_property src_info {type:XDC file:1 line:99 export:INPUT save:INPUT read:READ} [current_design]
set_property PACKAGE_PIN AF1 [get_ports {ddr3_dq[10]}]
set_property src_info {type:XDC file:1 line:105 export:INPUT save:INPUT read:READ} [current_design]
set_property PACKAGE_PIN AE4 [get_ports {ddr3_dq[11]}]
set_property src_info {type:XDC file:1 line:111 export:INPUT save:INPUT read:READ} [current_design]
set_property PACKAGE_PIN AE3 [get_ports {ddr3_dq[12]}]
set_property src_info {type:XDC file:1 line:117 export:INPUT save:INPUT read:READ} [current_design]
set_property PACKAGE_PIN AE5 [get_ports {ddr3_dq[13]}]
set_property src_info {type:XDC file:1 line:123 export:INPUT save:INPUT read:READ} [current_design]
set_property PACKAGE_PIN AF5 [get_ports {ddr3_dq[14]}]
set_property src_info {type:XDC file:1 line:129 export:INPUT save:INPUT read:READ} [current_design]
set_property PACKAGE_PIN AF6 [get_ports {ddr3_dq[15]}]
set_property src_info {type:XDC file:1 line:135 export:INPUT save:INPUT read:READ} [current_design]
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

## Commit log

2024-05-09 Initial project commit
    To set up the project.
    Main FPGA connection:
    fmc_la_p_00 <= sync;
    fmc_la_p_18 <= pulse;
    fmc_la_p_24 <= trigger_out;
    sync_ext <= fmc_la_p_32;
    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
    [FMC_breakout-B_Cu.gbr, FMC_breakout-B_Mask.gbr, FMC_breakout-B_Paste.gbr, FMC_breakout-B_Silkscreen.gbr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]
2024-05-28 Laser control
    Added laser control in sync_pulse_det_generator.v, its dependencies and GUI. Signal CW enables a continuous emission from the MZI, pulse_control enables the pulse
2024-06-28 det and sync
    -Major bug fixes
    -Laser control buttons
    -Data Adquisition from Det0 and Det1
    -Synchronization in between Alice and Bob
    -New lm7171 pcb
    [lm7171opamp-B_Cu.gbr, lm7171opamp-B_Mask.gbr, lm7171opamp-B_Paste.gbr, lm7171opamp-B_Silkscreen.gbr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]
2024-07-24 det to pin_04
    Hice un cambio del pin 24 (det) al pin 04
2024-07-24 det to pin 04
    Genere el bitstream para el cambio del pulso det al pin 04
2024-07-25 sync master
    Control DM estaba usando el sync_internal siempre, debido a que sync_pulse_det tenia como output sync y no sync_master... resuleto
2024-07-28 deleted blinking LEDs
    Now only LED 0 is connected to a signal. It has sync, so it serves as Alice/Bob identifier. Alice should be always blinking while Bob only blinks when he receives a signal from Alice
2024-07-31 Bitstream 31/07
    Creación del Bitstream para nuevas pruebas.
2024-08-21 fmc_32 -> fmc_15
    Hola cambie el puerto fmc_la_p_32 al puerto fmc_la_p_15 para el sync externo de Bob
2024-08-21 Fmc_15 -> Fmc_0_n
    Cambie el puerto de Bob (sync_ext) de fmc_15 al fmc_0_n, elegimos este por que no tiene una resistencia de 50 ohms
2024-09-05 Paso Delay a incremento de 5ns
    Cambie el incremento de saltos de 50 ns a saltos de 5 ns
2024-09-16 Changes in Vivado
    -Cambie parte del codigo de AccCuentas.v, lo que estaba antes lo deje comentado
    - Y en el top (Genesys2_VideoDemoR1.vhd) deje comentado la señal que no estamos ocupando que en este caso es EN que viene de AccCuentas
2024-09-24 Bitstream pin 32
    Genere el bitstream para el cambio del det 0, decidimos que ingresara a Bob por el pin 32 ya que este no posee una resistencia.
2024-10-05 idqube_V2
    fixed bugs on AccCuentas. Deje conectado el clk a det1
2024-10-08 Generacion BitStream
    Generacion del bitstream para poder solucionar el problema de oneshoot (creemos que es el culpable de que las cuentas en el fpga no se actualicen)
2024-10-25 Solucion Error AccCuentas
    Encontre algunos errores en la AccCuentas que arregle, faltaba declarar algunas variables
2024-10-25 Bitstream con correcion de error AccCuentas
    Genere de nuevo el bitstream, arregle algunas variables que no estaban definidas
2025-04-01 add new output
    Agregue n_18 como MZI y p_24 como Sync para el monitoreo usando un osciloscopio
2026-01-14 Cambio LCVMOS FMC 1.2 -> 3.3V
